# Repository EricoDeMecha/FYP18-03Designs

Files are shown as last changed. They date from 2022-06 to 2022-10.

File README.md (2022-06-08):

## Design and Fabrication of an Automated Discharge Collection Unit of a Synthetic Hdyro-Experimental Machine

Latex sources

### Usage
Run ```renamef``` in the source directory to rename the output file.
```bash
    renamef
```

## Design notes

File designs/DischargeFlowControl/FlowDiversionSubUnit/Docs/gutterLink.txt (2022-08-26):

https://www.pvcpipefitting.com/products/110mm-half-round-pvc-rain-gutter/

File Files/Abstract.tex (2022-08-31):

\addcontentsline{toc}{section}{Abstract}
\section*{Abstract}
\label{sec:}
\par
The synthetic hydro-experimental machine used for fluid mechanics experiments in the fluids lab at JKUAT uses a manual mechanical system in the collection of the discharge during experiments such as the determination of coefficient of discharge of the Venturi. The user is required to turn a $1\frac{3}{4} inch $ ball valve in steps determined by human intuition, and for every step,he/she is required to slide a metallic diverter to collect the discharge to a separate tank, and at the same time, to start measuring the temperature of the discharge, and the timer using an analog stop watch. This synchronism is necessary for precise data in the computation of the fluid flow properties but cannot be achieved by human. 
\par
This project intends to design and fabricate an automated discharge collection system to minimize this human error while maintaining the credibility of the experiment. A modular system has been designed comprising of three major units; a discharge flow control unit, a discharge handling unit, and an interface and control unit. Through a touch-LCD interface, the user will set either the time interval between steps in an experiment or the number of steps for an experiment. In either case, the system will automatically determine the other based on the calibration of a full step. An MG996R servo motor has been selected to control the flow in steps that can be less than $1^{0}$ and for every step, a LA-T8 micro-linear actuator has also been selected to drive an oscillating flap through a four-bar kinematic chain. The flap diverts the flow to a discharge collection tank where its temperature and weight are measured using the selected DS18B20 temperature sensor, and four 50Kg strain type load cells connected in a WheatStone bridge respectively. The data for every step are displayed on the interface. The collected discharge is then emptied to the main reservoir through a solenoid valve before the next step.

\par
This automation will reduce the error margin in the computation of fluid flow properties due to the human error.

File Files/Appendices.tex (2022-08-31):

\appendix
\section{Appendix}

\subsection{Nema 17 Stepper motor dimensions}
    \begin{figure}[H]
        \centering
        
        \caption{Nema 17 Stepper Motor Drawing}
    \end{figure}

\subsection{Ball valve dimensions}
    \begin{figure}[H]
        \centering
        
        \caption{Ball valve socket}
    \end{figure}

\subsection{MG996R Servo motor dimensions}
\begin{figure}[H]
    \centering
    
    \caption{MG996R Servo Motor}
\end{figure}

\subsection{Synthetic Hydro Experimental Machine in JKUAT}
\begin{figure}[H]
    \centering
    
    \caption{S.H.E.M relevant machine dimensions}
\end{figure}

\subsection{Semester 1 \& 2 Time Plan}

\begin{table}[H]
\centering
\begin{tabular}{|ll|l|l|l|l|l|l|l|l|l|l|}
\hline
\multicolumn{1}{|l|}{\textbf{Week}} & \textbf{1} & \textbf{2} & \textbf{3} & \textbf{4} & \textbf{5} & \textbf{6} & \textbf{7} & \textbf{8} & \textbf{9} & \textbf{10} & \textbf{11} \\ \hline
\multicolumn{1}{|l|}{Project proposal} &  & \cellcolor[HTML]{656565}{\color[HTML]{656565} } & \cellcolor[HTML]{656565}{\color[HTML]{656565} } & \cellcolor[HTML]{656565}{\color[HTML]{656565} } &  &  &  &  &  &  &  \\ \hline
\multicolumn{1}{|l|}{Continuous Presentation} &  &  &  &  & \cellcolor[HTML]{656565} & \cellcolor[HTML]{656565} & \cellcolor[HTML]{656565} & \cellcolor[HTML]{656565} & \cellcolor[HTML]{656565} & \cellcolor[HTML]{656565} & \cellcolor[HTML]{656565} \\ \hline
\multicolumn{1}{|l|}{Literature review} &  &  &  &  &  & \cellcolor[HTML]{656565} & \cellcolor[HTML]{656565} & \cellcolor[HTML]{656565} & \cellcolor[HTML]{656565} & \cellcolor[HTML]{656565} & \cellcolor[HTML]{656565} \\ \hline
\multicolumn{1}{|l|}{Discharge flow control design} &  &  &  &  &  & \cellcolor[HTML]{656565} & \cellcolor[HTML]{656565} & \cellcolor[HTML]{656565} & \cellcolor[HTML]{656565} & \cellcolor[HTML]{656565} &  \\ \hline
\multicolumn{2}{|l|}{Discharge   collection unit design} &  &  &  &  &  & \cellcolor[HTML]{656565} & \cellcolor[HTML]{656565} & \cellcolor[HTML]{656565} & \cellcolor[HTML]{656565} &  \\ \hline
\multicolumn{1}{|l|}{Interface and control design} &  &  &  &  &  &  &  &  & \cellcolor[HTML]{656565} & \cellcolor[HTML]{656565} & \cellcolor[HTML]{656565} \\ \hline
\multicolumn{1}{|l|}{Assembly and testing} &  &  &  &  &  &  & \cellcolor[HTML]{656565} & \cellcolor[HTML]{656565} & \cellcolor[HTML]{656565} & \cellcolor[HTML]{656565} &  \\ \hline
\multicolumn{1}{|l|}{Interim report} &  &  &  &  &  &  &  &  & \cellcolor[HTML]{656565} & \cellcolor[HTML]{656565} & \cellcolor[HTML]{656565} \\ \hline
\multicolumn{1}{|l|}{Final presentation} &  &  &  &  &  &  &  &  &  &  & \cellcolor[HTML]{656565} \\ \hline
\end{tabular}
\caption{Semester 1 timeplan}
\end{table}

\begin{sidewaystable}
\centering
\caption{Semester 2 Timeplan}
\resizebox{\linewidth}{!}{%
\begin{tabular}{|>{\hspace{0pt}}m{0.392\linewidth}|>{\hspace{0pt}}m{0.035\linewidth}|>{\hspace{0pt}}m{0.035\linewidth}|>{\hspace{0pt}}m{0.035\linewidth}|>{\hspace{0pt}}m{0.035\linewidth}|>{\hspace{0pt}}m{0.035\linewidth}|>{\hspace{0pt}}m{0.035\linewidth}|>{\hspace{0pt}}m{0.035\linewidth}|>{\hspace{0pt}}m{0.035\linewidth}|>{\hspace{0pt}}m{0.035\linewidth}|>{\hspace{0pt}}m{0.035\linewidth}|>{\hspace{0pt}}m{0.035\linewidth}|>{\hspace{0pt}}m{0.035\linewidth}|>{\hspace{0pt}}m{0.035\linewidth}|>{\hspace{0pt}}m{0.035\linewidth}|>{\hspace{0pt}}m{0.035\linewidth}|} 
\hline
\textbf{Week} & \textbf{14} & \textbf{15} & \textbf{16} & \textbf{17} & \textbf{18} & \textbf{19} & \textbf{20} & \textbf{21} & \textbf{22} & \textbf{23} & \textbf{24} & \textbf{25} & \textbf{26} & \textbf{27} & \textbf{28} \\ 
\hline
Design for fabrication & {\cellcolor[rgb]{0.471,0.471,0.471}} &  &  &  &  &  &  &  &  &  &  &  &  &  &  \\ 
\hline
Generating fabrication files & {\cellcolor[rgb]{0.471,0.471,0.471}} & {\cellcolor[rgb]{0.471,0.471,0.471}} &  &  &  &  &  &  &  &  &  &  &  &  &  \\ 
\hline
Procurement of fabrication materials &  & {\cellcolor[rgb]{0.471,0.471,0.471}} & {\cellcolor[rgb]{0.471,0.471,0.471}} &  &  &  &  &  &  &  &  &  &  &  &  \\ 
\hline
Procurement of electrical and electronics components &  &  & {\cellcolor[rgb]{0.471,0.471,0.471}} & {\cellcolor[rgb]{0.471,0.471,0.471}} &  &  &  &  &  &  &  &  &  &  &  \\ 
\hline
Fabrication of the discharge flow control unit(DFCU) &  &  & {\cellcolor[rgb]{0.471,0.471,0.471}} & {\cellcolor[rgb]{0.471,0.471,0.471}} & {\cellcolor[rgb]{0.471,0.471,0.471}} &  &  &  &  &  &  &  &  &  &  \\ 
\hline
Writing drivers and firmware for the electronics in DFCU &  &  &  &  & {\cellcolor[rgb]{0.471,0.471,0.471}} & {\cellcolor[rgb]{0.471,0.471,0.471}} &  &  &  &  &  &  &  &  &  \\ 
\hline
Assembly and testing of the DFCU &  &  &  &  &  &  & {\cellcolor[rgb]{0.471,0.471,0.471}} &  &  &  &  &  &  &  &  \\ 
\hline
Fabrication of the discharge handling unit(DHU) &  &  &  &  &  &  &  & {\cellcolor[rgb]{0.471,0.471,0.471}} & {\cellcolor[rgb]{0.471,0.471,0.471}} & {\cellcolor[rgb]{0.471,0.471,0.471}} &  &  &  &  &  \\ 
\hline
Writing drivers and firmware for the electronics in DHU &  &  &  &  &  &  &  &  &  & {\cellcolor[rgb]{0.471,0.471,0.471}} & {\cellcolor[rgb]{0.471,0.471,0.471}} &  &  &  &  \\ 
\hline
Assembly and testing of the DHU &  &  &  &  &  &  &  &  &  &  &  & {\cellcolor[rgb]{0.471,0.471,0.471}} &  &  &  \\ 
\hline
Development of the LCD driver and GUI &  &  &  &  &  &  &  &  &  &  &  & {\cellcolor[rgb]{0.471,0.471,0.471}} & {\cellcolor[rgb]{0.471,0.471,0.471}} &  &  \\ 
\hline
Assembly and testing of the system &  &  &  &  &  &  &  &  &  &  &  &  &  & {\cellcolor[rgb]{0.471,0.471,0.471}} &  \\ 
\hline
Final Presentation &  &  &  &  &  &  &  &  &  &  &  &  &  &  & {\cellcolor[rgb]{0.471,0.471,0.471}} \\
\hline
\end{tabular}% <-- Remember this
}
\end{sidewaystable}

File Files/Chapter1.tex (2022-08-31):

\section{Introduction}
\label{sec:introduction}
\subsection{Background}
Fluid flow measurement involves the measurement of the properties of a smooth and uninterrupted stream of flowing particles that conform to a pipe. These flow properties include the coefficient of discharge, mass flow rate, fluid velocity, differential pressure, and conductivity coefficients \cite{pereira2009flow}. They are altered and measured by flow measuring devices such as the Venturi, the Orifice, turbine flow meters and rotameters \cite{nandagopal2022fluid}. These measurements are finally related to the flow using the Bernoulli's equation. 

\par
The Synthetic Hydro-Experimental machine, currently installed in JKUAT, is a configurable machine with these flow meters. This machine is used to conduct experiments to establish relationships between the fluid flow properties and the behavior of the flow. It has a lift pump, gate valves, alcohol manometers, pressure gauges, a Pelton turbine, a Venturi, an orifice, and water reservoirs.  During experiments, the lift pump is turned on, and the discharge valve is fully opened to establish a steady flow.  The discharge valve is then closed. The valve is opened in small steps depending on the number of steps required. For each step, the discharge is collected, and its temperature is measured within a specific time interval. Finally, the weight of the collected discharge is also measured.

\subsection{Problem statement}

In fluid flow experiments utilizing the Venturi and the orifice to establish the coefficient of discharge, the discharge steps must be precisely opened, and time and temperature measurements must be made concurrently with discharge collection so as to achieve values that are within a reasonable range.The Synthetic Hydro-Experimental machine now in use at JKUAT to establish this relationship, however, is entirely mechanical, making it impossible for a human to do some of the simultaneous measurements. A ball valve regulates the flow rate in small intervals using human intuition, which can be imprecise. As a result, with these discrepancies, the findings might frequently be outside of the acceptable range. Automating the discharge collection process can minimize the error in the results and still preserve the credibility of the experiment.

\subsection{Objectives}
\subsubsection{Main objective}

 To automate the discharge collection process for the Synthetic Hydro-Experimental machine. 

\subsubsection{Specific objectives}

\begin{enumerate}
	\item To design an automated discharge flow control unit that can turn the ball valve in steps of less than $1^{0}$ and divert the flow in less than 1 second.
	\item To design and fabricate a discharge handling unit with automated weight, time and temperature measurements, and a discharge collection tank that can discharge is the least time possible.
    \item To design a graphical user interface and a robust control algorithm to integrate the units.

\end{enumerate}

\subsubsection{Expected outcomes}
A unit with a discharge flow control mechanism that can turn in steps of less than $1^{0}$. Furthermore, to accurately regulate the flow of the discharge into either the collecting tank or into the main reservoir, the mechanism should be able to divert the flow from the pipeline in less than a second. The discharge should then be collected in a  tank that can store up to $0.02m^{3}$ of the discharge. A weight measurement device with a gauge factor of more than 2 to be attached at the bottom of the collection tank.Finally, a graphical user interface that allows for the displaying of measurements in this case temperature, time and weight and control of operations

% \begin{enumerate}
%     \item \textbf{Discharge flow control unit}
%     \begin{itemize}
%         \item \textbf{Flow control subunit}-  A discharge flow control mechanism that can turn steps less than $1^{0}$. This is necessary in a case where an experiment is to be done in more than 90 steps( less than $1^{0}$ per step). 
%         \item \textbf{Diversion subunit} - A mechanism that can divert the flow in less than a second. This is to ensure that only the flow within the time interval is collected.
%     \end{itemize}
%     \item \textbf{Discharge Handling unit}
%     \begin{itemize}
%         \item \textbf{Discharge collection tank}  - A tank that can collect up to $0.02m^{3}$ of the discharge. This is an estimated quantity of the discharge collected when the valve is fully open for approximately 30 seconds.
%         \item \textbf{Discharge Weight measurement} -  A weight measurement device with a gauge factor of more than 2. This is necessary to detect even the smallest change in weight.
%         \item \textbf{Discharge temperature measurement} - An immersible temperature sensor with a resolution of more than 10 bits. This is necessary to detect even the smallest change in the temperature of the discharge.
%         \item \textbf{Outlet valve} - Approximately 1 inch valve in order to empty the empty approximately $0.02m^{3}$ in the least time possible. 
%     \end{itemize}
%     \item \textbf{Interface and Control Unit}
%     \begin{itemize}
%         \item \textbf{Micro-controller} - A microcontroller that can drive a 320x240 touch LCD at approximately 30 frames per second. This is to ensure the displayed data is updated on time while maintaining a slick graphical user interface. 
%         \item \textbf{Application logic} - A robust application logic with auto-calibration capabilities, and event-driven. 
%     \end{itemize}

% \end{enumerate}

\subsection{Justification}
This automation will streamline the discharge collecting process while also ensuring the consistency and quality of the data collected in each phase of the fluid flow tests performed on the system. In contrast to the existing condition, such automation allows a single person to perform the experiment without significant effort. Furthermore, the automated system will also be modular, allowing it to be readily attached and detached from the main machine with few modifications.

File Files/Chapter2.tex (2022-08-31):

\section{Literature Review}
\subsection{Introduction}
Fluid flow experiments involve determination of the flow velocity, the mass flow rate or volumetric flow rate. These experiments are used to familiarize the students with typical methods of flow measurement of an incompressible fluid and, at the same time demonstrate applications of the Bernoulli's equation. Thus, these experimental investigations require the application of measuring techniques to yield quantitative information on the relationship between pressure, temperature and local flow velocities.
\par
The synthetic hydro-experimental machine employs the use of the venture and the orifice meter in determining these fluid properties specifically the coefficient of discharge. It involves determining the relationship between a flowing fluid through a valve, the weight and temperature of the collected discharge. The machine comprises of four main parts; the diverter, gate valve, weight and temperature measurement unit. The measurement involves four main processes, discharge collection, diversion, weight and temperature measurement. 
\subsubsection{Gate Valve }
\par
The valve is attached at the end of the pipeline immediately after the venture and the orifice meter. It is used in flow rate control by either increasing or reducing the aperture at which the fluid flows. The experiment is conducted in several steps which is determined by opening and closing of the valve. At the start of the experiment, the valve is initially closed hence no fluid is collected. Depending on the required number of steps, the valve is then opened in small steps allowing the discharge to be collected for purposes of weight and temperature measurement.
\subsubsection{Diverter }
\par
After each step of the experiment, the collected fluid flows into the weight measurement unit through the help of a diverter. The diverter is used to direct the collected discharge into the weight measurement unit which is located at the periphery of the rig to avoid flowing back into the reservoir. The diverter is a mechanical device that is moved by hand.
\subsubsection{Temperature measurement unit }
\par
 The temperature of the collected discharge is measured immediately after the fluid flows through the gate valve by use of a thermometer. This is to minimize the environmental effects, for instance the effects of the metallic diverters which would otherwise compromise on the temperature readings. The readings are measured and recorded after each step of the experiment.
\subsubsection{Pressure measurement }
\par
The differential manometers are attached just before and after both the venture and the orifice and is used to determine the pressure of the flowing fluid. These manometric readings are recorded after each and every step of the experiment.
\subsubsection{Weight measurement unit }
\par
The final part involves measuring the weight of the collected discharge. This is done by use of a measuring scale with loads attached to it. The above measurements are then used to establish the coefficient of discharge of the fluid.
\subsection{Existing Technologies}
Some advanced and even rudimentary technologies have been used in place of the Synthetic Hydro-Experimental machine for the determination of fluid flow properties. The technologies include :   
\subsubsection{Computational Fluid Dynamics}
Computational fluid dynamics(CFD) is a powerful modelling and analysis technique that utilizes finite difference techniques to solve highly non-linear differential equation of pressure, energy, relative humidity, air temperature and velocity \cite{raman2018review}. It can be used to model fluid flow in flow measurement devices.
\par
Tukimin et al \cite{tukimin2016cfd} in their study  conducted a CFD analysis using an Single Kernel Estimate (SKE) turbulence model to determine the coefficient of discharge of a Venturi tube, and finally compared the results to those obtained from a physical experimental setup. The test loop shown in figure \ref{fig:test_loop_rig} was used both in a physical setup and a CFD model. 

\begin{figure}[ht]

\centering
\caption[Test loop schematic]{ Test loop schematic by Tukimin et al \cite{tukimin2016cfd}}
\label{fig:test_loop_rig}
\end{figure}

They designed a CFD model using the ANSYS Design Modeller software. The model consists of a Venturi tube, designed according to the standards ISO 5167:2003 \cite{carello2013flow}, and a liquid and gas system. They did a physical experiment using the same test matrix used in the numerical simulation model. Finally, they computed the coefficient of discharge of the venturi using equation \ref{eq:2}.  

\begin{equation}
C d=\frac{4 m \sqrt{1-\beta^{4}}}{\pi \varepsilon d^{2} \sqrt{200000 D p_{1} \rho_{1}}}
\label{eq:2}
\end{equation}

\begin{table}[!t]
  \begin{center}
    \leavevmode
    \hangcaption{ Calculated $C_{d}$}   
     \begin{tabular}{rlc}\hline
      Venturi under Test & Average Discharge Coefficient &  Average Discharge Coefficient \\ \hline
       & From experiment &  From CFD post \\ \hline
      Venturi 1 & 0.99366 &  0.984347 \\ \hline
    \end{tabular}
    \label{tab:cd}
  \end{center}
\end{table}
The results obtained in \ref{tab:cd} showed a difference of less than $1 \%$ between the $C_{d}$ obtained from the two setups.
\par
Tamhankar et al \cite{tamhankar2014experimental} also did a similar experiment using a CFD model designed in ANSYS Fluent 13.0 utilizing a Realizable k-$\epsilon$ turbulence model which is superior to a Standard k-$\epsilon$ turbulence model and compared the results to those obtained from an experimental setup show in figure \ref{fig:exp}. 

\begin{figure}[ht]

\centering
\caption[Experimental setup ]{ Experimental setup by Tamhankar et al \cite{tamhankar2014experimental}}
\label{fig:exp}
\end{figure}

Table \ref{tab:results} shows the results obtained from the study
\begin{table}[!t]
    \centering
    \hangcaption{Results}
    \begin{tabular}{|c|c|c|}
        \hline \text { Reading No. } & \text { Experiment } & \text { CFD analysis } \\
        \hline 1 & 0.9724 & 0.9619 \\
        \hline 2 & 0.9592 & 0.9689 \\
        \hline 3 & 0.9779 & 0.9692 \\
        \hline
    \end{tabular}
    \label{tab:results}
\end{table}

The study concluded that difference in values of the coefficient of discharge obtained from the model and those obtained from the experimental setup was less than $ 5 \%$ .
\subsubsection{Analytical Predictions}
This technique utilizes the Bernoulli's equation to establish an analytical correlation between the fluid flow and the coefficient of discharge of the Venturi meter. 

\begin{figure}
    \centering
    
    \caption[Venturi Meter]{Venturi meter \cite{venturi_meter}}
    \label{fig:venturi}
\end{figure}

Figure \ref{fig:venturi} shows the Venturi meter. Assuming the flow is ideal and applying the Bernoulli's equation before and after the contraction, 

\begin{equation}
\begin{aligned}
&\frac{p_{1}}{\rho g}+\frac{v_{1}^{2}}{2 g}+z_{1}=\frac{p_{2}}{\rho g}+\frac{v_{2}^{2}}{2 g}+z_{2} \\
&\text { But } Z_{1}=Z_{2}, \\
&\frac{\left(p_{1}-p_{2}\right)}{\rho}=\frac{\left(v_{2}^{2}-v_{1}^{2}\right)}{2} \\
&\frac{\left(p_{1}-p_{2}\right)}{\rho}=\frac{v_{2}^{2}}{2}\left(1-\frac{A_{2}^{2}}{A_{1}^{2}}\right) \\
&\frac{\Delta p}{\rho}=\frac{v_{2}^{2}}{2}\left(1-\beta^{4}\right) \\
&v_{2}=\frac{1}{\sqrt{1-\beta^{4}}} \sqrt{\frac{2 \Delta p}{\rho}}
\end{aligned}
\label{eq:bernoulli_der}
\end{equation}

Applying the continuity equation to the result of the derivation in \ref{eq:bernoulli_der},
\begin{equation}
\begin{aligned}
&Q_{t h}=A_{1} v_{1}=A_{2} v_{2} \\
&Q_{t h}=A_{2} v_{2}=\frac{1}{\sqrt{1-\beta^{4}}} \frac{\pi d^{2}}{4} \sqrt{\frac{2 \Delta p}{\rho}}
\end{aligned}
\label{eq:mass_flow_rate}
\end{equation}
Equation \ref{eq:mass_flow_rate} of theoretical flow rate is based on the assumption that the flow is steady, incompressible, inviscid, irrotational, no losses and the velocities $V_{1}$ and  $V_{2}$ are constant across the cross section \cite{arun2015prediction}. 

\begin{equation}
\mathrm{Q}_{\mathrm{act}}=\frac{\mathrm{C}_{\mathrm{d}_{\mathrm{st}} \mathrm{d}}}{\sqrt{1-\beta^{4}}} \frac{\pi \mathrm{d}^{2}}{4} \sqrt{\frac{2 \Delta \mathrm{p}}{\rho}}
\end{equation}
The frictional and viscous losses in a laminar flow can be estimated by the Darcy's law
\begin{equation}
\mathrm{H}_{\mathrm{L}}=\frac{(\Delta \mathrm{p})_{\text {viscous }}}{\rho \mathrm{g}}=\mathrm{f} \frac{\mathrm{v}^{2}}{2 \mathrm{~g}} \frac{\mathrm{D}}{\mathrm{D}}
\end{equation}
where 'f' is the friction factor.
\par
Coefficient of discharge equation \ref{eq:cd2} where for laminar flow, 'f' is given by equation \ref{eq:f} . This equation is derived from both the Darcy's law equation and the theoretical flow rate equation \ref{eq:mass_flow_rate}.
\begin{equation}
f=\frac{64}{R_{e d}}
\label{eq:f}
\end{equation}

\begin{equation}
C_{\mathrm{d}}=0.995 \sqrt{\frac{1}{(1+3 f)}}
\label{eq:cd2}
\end{equation}

\par
Arun et al \cite{arun2015prediction} did  a comparision of the $C_{d}$ obtained by this method and that obtained from a CFD simulation. The study concluded that the results from the two methods had an uncertainty of $0.9\%$.
\subsection{Related Works}
Discharge collection techniques have been developed for various applications. Some of these applications are related to the discharge collection unit used in the Synthetic Hydro-Experimental machine.

\subsubsection{Electromagnetic activation}
Angelo et al \cite{odetti2019design} implemented this technique in the design and testing of an Modular Automatic Water Sampler(MAWS). They designed MAWS and mounted them on unmanned marine vehicle with the aim of collecting water samples for scientific campaigns in front of polar tidewater glaciers. Their main design considerations was the response time of the stopper since the MAWS were operated under water and at the risk of damage by glaciers. The actuation unit of the sampler is shown in figure \ref{fig:stopper}. 

\begin{figure}
    \centering
    
    \caption[Sampler actuation mechanism]{Sampler actuation mechanism \cite{odetti2019design}}
    \label{fig:stopper}
\end{figure}

When the coil in the solenoid is crossed by a current a strong magnetic field is generated that attracts the ferromagnetic plunger connected to the sealing stopper and opens the bottle allowing water to flow into the bottle's neck. As the current stops the two permanent magnets attract each other and the stopper seals the bottle \cite{odetti2019design}.

\subsubsection{Pneumatic Control}
Pneumatic actuators utilizes the power of compressed air to impart motion on objects. Sangmin, and Joonwon \cite{lee2009development} did a design of cartridge-type pneumatic dispenser with a back flow stopper. The system used a membrane covering a discharge hole. The membrane was opened and closed using negative and positive pneumatic pressure respectively as shown in figure \ref{fig:dispensing_mechanisml}. 

\begin{figure}
    \centering
    
    \caption[Dispensing mechanism]{Dispensing mechanism \cite{lee2009development}}
    \label{fig:dispensing_mechanisml}
\end{figure}

The application was able to do precise dispensation of 100nL to 400nL droplets.

\subsection{Summary}

Every fluid flow experiment done on the Synthetic Hydro-Experimental machine involves the collection of discharge and the measurement of its properties. The most common experiment is the determination of the coefficient of discharge  of the Venturi and the Orifice. In this literature, other techniques such as CFD and analytical methods have been found to be effective as alternatives to this machine. These techniques have been proven to produce results with a difference of less than $1\%$  from the experimental results obtained from a physical setup. Such results can also be obtained from the fluids rig currently used in JKUAT by automating the discharge collection unit. With regard to this, the literature has also covered discharge collection techniques that have proven to be effective in other applications and can be adapted for this automation. This techniques include the application of pneumatics and electromagnetism. 

\subsection{Gap analysis}
\begin{enumerate}
    \item The use of the CFD method or the analytical method  undermines the credibility of the fluid flow experiments. This two techniques are rather used for the design of fluid flow measuring devices.
    \item CFD method can also be very resource intensive in terms of compute resources. Softwares used for this method requires a hefty license fee.
    \item The application of the analytical method involves tedious calculations and several assumptions which can produce untrustworthy results.
    \item The use of the Synthetic Hydro-Experimental machine with a manual discharge collection unit often produce results with huge error margins.  
\end{enumerate}

This project is entirely focused on addressing gap number four with the application of techniques such as pneumatics or electromagnetism. This closes in the technological gap with the use of CFD, and simplify the use of analytical methods by providing data for the computation of fluid flow properties.

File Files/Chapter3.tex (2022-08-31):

\section{Methodology}
\subsection{Overview}
This project consists of three main units: a discharge flow control unit, a discharge handling  unit, and a software and control unit. 
\subsection{Discharge flow control unit}
This unit consist of two main sub-units:
\begin{enumerate}
    \item \textbf{Flow control sub-unit} -
    This sub-unit controls the dispensing of the discharge from the discharge pipe in steps.
    \item \textbf{Flow diversion sub-unit} -
    This sub-unit diverts the discharge from the main discharge pipe either to the discharge collection tank or to the main reservoir.
\end{enumerate}
\par
\subsubsection{Flow control  sub-unit}
The current state-of-art of this unit is as shown in Figure \ref{fig:current_discharge_control_unit}. 
\begin{figure}[H]
    \centering
    
    \caption{Current discharge control unit}
    \label{fig:current_discharge_control_unit}
\end{figure}
\par
The $1 \frac{3}{4} inch $ ball valve on the main discharge pipe is opened in steps by hand using the lever. The size of a step is determined by intuition.
\par
\textbf{Design}\\
To ensure minimum modification of the existing machine, the automation of this unit utilized the existing ball valve. The opening and closing of the valve is automated using a motorized system that can open the valve in precise steps.
\par
\textbf{Motor}
\par
The selection and the sizing of the motor for this application was based on the following considerations:

\begin{enumerate}
    \item The torque required to open and close the ball valve.
    \item The steps size or the number of steps the system can open the valve.
\end{enumerate}
\par
Based on these two considerations, the following two applications were considered.
\begin{enumerate}
    \item \textbf{Stepper motor application}\\
    This motor operates by accurately synchronizing position with the pulse signal output from the controller to the driver thus achieving highly accurate positioning and speed control. Stepper motors feature high torque and low vibration at low speeds ideally below 1500rpm, ideal for applications requiring quick fixed positioning in a short distance \cite{wargula2017investigations}. Furthermore, stepper motor rotates with a fixed step angle typically 1.8 degrees for a 2-phase. However, to achieve this requires the use of a micro-step driver.
    \par
    Besides having full control of rotation and speed, the simple structure of stepper motors is achieved without using electrical components, such as an encoder within the motor. For this reason, stepper motors are very robust and have high reliability with very few failures. As for stopping accuracy, ±0.05° (without cumulative pitch errors) is very accurate\cite{wargula2017investigations}. Because the positioning of stepper motors is performed by open-loop control, and operated by the magnetized stator and magnetic rotor with small teeth, stepper motors have a higher follow-up mechanism toward commands than the servo motors. Also, no hunting occurs when stopping it.
    
    \textbf{Design with stepper motor}
    \begin{enumerate}
    \item \textbf{Motor selection}\\
    From the stepper motors available in the market, Nema 17 Stepper motor shown in figure \ref{fig:Nema17 Steppper motor} was the best choice for the job since it can produce a $1.8^0$ step out of the box without a microstep driver. With the help of a microstep driver, it can produce as small as $1^0$ step.
    \begin{figure}[H]
        \centering
        
        \caption[Nema 17 Stepper motor]{Nema 17 Stepper motor \cite{nema17}}
        \label{fig:Nema17 Steppper motor}
    \end{figure}
    \par
    Its technical specifications are as shown in the table \ref{tab:nema17_specs}:
\begin{longtable}{|l|l|}
\caption[Nema 17 Stepper Motor Technical specification]{Nema 17 Stepper Motor Technical specifications \cite{nema17}}
\label{tab:nema17_specs}\\
\hline
\textbf{Property} & \textbf{Value} \\ \hline
\endfirsthead
%
\multicolumn{2}{c}%
{{\bfseries Table \thetable\ continued from previous page}} \\
\hline
\textbf{Property} & \textbf{Value} \\ \hline
\endhead
%
Rated Voltage & 12V DC \\ \hline
Current & 1.2A at 4V \\ \hline
Step Angle & 1.8 deg \\ \hline
No. of Phases & 4 \\ \hline
Motor Length & 1.54 inches \\ \hline
4-wire, 8 inch lead &  \\ \hline
steps per revolution & 200 \\ \hline
Operating Temperature & -10 to 40 °C \\ \hline
Unipolar Holding Torque & 22.2 oz-in \\ \hline
Maximum torque & 4.8 Kg.cm \\ \hline
\end{longtable}

    \item \textbf{Ball valve - motor interface}
    \par
    An interface is required to connect the motor rotor to the ball valve. The following  two design options were considered for this application:
    \begin{itemize}
        \item An interface that could fit the rotor on one end and with claw-like fingers on the other end to turn the existing ball valve's lever.
        \item An interface that could fit the rotor on one end and with the other end, similar to the lever, that could be used in place of the lever.
    \end{itemize}
    \par
    The second option was chosen since the first choice will introduce a lag in a turn action since the point of action on the lever is displaced from the line of rotation of the rotor.
    \begin{figure}[H]
        \centering
        
        \caption{Interface}
        \label{fig:Interface}
    \end{figure}
    Figure \ref{fig:Interface} shows the interface design. Dimensions of the interface, such as the width of its base, were measured and transferred from the existing lever.
    \par
    \item \textbf{Motor cage}
    \par
    In order to support the motor on the ball valve, a motor cage was designed to fit the motor as shown in Figure \ref{fig:motor_cage_stepper}.
    
    \begin{figure}[H]
        \centering
        
        \caption{Motor Cage}
        \label{fig:motor_cage_stepper}
    \end{figure}
    
    The dimensions of the motor cage in figure \ref{fig:motor_cage_stepper} were determined from that of the stepper motor, the motor-ball valve interface, and that of the existing ball valve socket in order to fit the socket.
    
    \item \textbf{Straps}
    \par
    The motor cage with the stepper motor mounted is mounted on the main discharge pipe using straps, one of which is shown in figure \ref{fig:mounting_straps_stepper}.
    
    \begin{figure}[H]
        \centering
        
        \caption{Mounting straps}
        \label{fig:mounting_straps_stepper}
    \end{figure}
 \item \textbf{Assembly of discharge flow control using stepper}
    \par
    The assembly of the discharge control unit is as shown in figure \ref{fig:stepper_actuated_ball_valve}. Nuts are used to fasten the whole structure on the main discharge pipe.
    
    \begin{figure}[H]
        \centering
        
        \caption{Stepper Actuated ball valve}
        \label{fig:stepper_actuated_ball_valve}
    \end{figure}
    
    % \item \textbf{Finite element analysis of the assembly}
    % \par
    % The assembly was stress tested by applying a torque on the motor cage to determine if it could hold at the maximum torque of the motor. To do this, each part of this assembly was be assigned a material. Polyactic acid (PLA) was selected as the common material for all of the parts in the assembly. This is majorly due to the following reasons:
    % \begin{itemize}
    %     \item The maximum weight of the part to be supported by the structure is the stepper motor's weight, 450 grams. This can be supported by a 3D printed plastic support. A lighter material such as fiber glass or carbon fiber could be used but they are costlier than the set project's budget.
    %     \item The parts are complex for fabrication on the currently existing machinery in the university.
    % \end{itemize}
    % \item \textbf{Results}
    % \par
    % As shown in figure \ref{fig:SimulationResults}, the structure holds for the maximum torque of a Nema 17 stepper motor, $4.9 kg.cm$ or $0.4707192 Nm$.
    % \begin{figure}[H]
    %     \centering
    %     \includegraphics[width=\textwidth]{Figures/ActuatedBallValve-Static-1-1-1.png}
    %     \caption{Simulation results}
    %     \label{fig:SimulationResults}
    % \end{figure}

    \end{enumerate}

    \item \textbf{Servo motor application}\\
    Servo motors run significantly faster than stepper motors, with speeds greater than 1500 rpm \cite{halicioglu2016mechanisms}. This enables servomotors to be used with gearboxes to deliver much higher torque at useful speeds. They also deliver more consistent torque across the speed range of the motor. Unlike stepper motors, they do not have holding torque. Closed-loop operation enables the controller/drive to command that the load remain at a specific position, however, and the motor will make continual adjustments to hold it there. Thus, servomotors can produce de facto holding torque\cite{halicioglu2016mechanisms}. The Servo motor rotates with a fixed step angle as low as 1 degree with or without the use of a driver. Furthermore, when powered, servomotors tend to move their shaft position to zero, a phenomenon known as hunting.
    \par
    \textbf{Design with servo motor}
    \begin{enumerate}
    \par
    \item \textbf{Motor selection}
    \par
    An MG996R Servo motor shown in figure \ref{fig:servo_motor_assembly} was the best choice among many servo motors found in the market. It is the motor that provided the torque required to turn the ball valve at an optimum price for the project's budget. 
    \par
    The motor specification as shown in table \ref{tab:MG996R_servo_specs}.
    \begin{table}[H]
    \centering
    \caption[MG996R Servo motor specifications]{MG996R Servo motor specifications \cite{mg996r}}
    \begin{tabular}{|l|l|}
    \hline
    \textbf{Property} & \textbf{Value} \\ \hline
    Operating Voltage & +5V \\ \hline
    Current & 2.5A (6V) \\ \hline
    Stall Torque & 9.4 kg/cm (at 4.8V) \\ \hline
    Maximum Stall Torque & 11 kg/cm (6V) \\ \hline
    Operating speed & 0.17 s/60° \\ \hline
    Gear Type & Metal \\ \hline
    Rotation & 0°-180° \\ \hline
    Weight of motor & 55gm \\ \hline
    \end{tabular}
    \label{tab:MG996R_servo_specs}
    \end{table}
    \begin{figure}[H]
        \centering
        
        \caption[MG996R servo motor]{MG996R servo motor \cite{mg996r}}
        \label{fig:servo_motor_assembly}
    \end{figure}
    The mounting mechanism of a servo motor is not as direct as that of the stepper motor since a servo motor homes to $0^{0}$ on powering. It is required that the home position of the servo motor is equal to the closed position of the ball valve. Therefore, during mounting, the servo motor must be rotated to align its home position with the closed position of the ball valve.
    \par
    The mounting mechanism should therefore allow for this rotation. A cuboid cage could have been used to support the motor in place, but since the centre of mass of this motor is displaced from its line of axle rotation, rotating the cuboid could mean repositioning the support stands for the cuboid.
    \par
     There were two options that could achieve this kind of rotation:
     \begin{enumerate}
         \item A combination of a cuboid cage on a circular plate. The cuboid cage could hold the motor while the plate allows the rotation of the assembly of the two without the need of repositioning the stands holding the assembly on the ball valve.
         \par
         \textbf{Designs with this approach}
         \par
         \begin{itemize}
             \item \textbf{Servo motor cage}
            \par
            The cage shown in figure \ref{fig:servo_motor_cage} is screwed on to the motor flaps. It just adds additional mounting points for the motor. 
            \begin{figure}[H]
                \centering
                
                \caption{Servo motor cage}
                \label{fig:servo_motor_cage}
            \end{figure}
            \par
            % \item \textbf{Mounting plate}
            % \par
            % Figure \ref{fig:servo_motor_mounting_plate} shows the mounting plate for the motor cage. The plate is like a ring with slots. The design allows for rotation without the need to reposition the supporting rods. 
            % \par
            % \begin{figure}[H]
            %     \centering
            %     \includegraphics[height=.7\textheight]{Figures/ServoMotorHolderMount.PNG}
            %     \caption{Servo motor mounting plate}
            %     \label{fig:servo_motor_mounting_plate}
            % \end{figure}
            \par
            \item \textbf{The holder assembly}
            \par
            Figure \ref{fig:servo_motor_mounted_assembly} shows the servo motor cage with the servo motor mounted on the mounting plate. The servo motor assembly can be rotated and translated to reposition the line of rotation of the motor axle. 
            \begin{figure}[H]
                \centering
                
                \caption{Servo motor mounted assembly}
                \label{fig:servo_motor_mounted_assembly}
            \end{figure}
             This design can allow for both rotational and translational adjustments along the slots. However, it is complex and require a lot of fasteners.
         \end{itemize}
         \item A combination of spur gears to always translate the line of rotation of the motor axle to a fixed line of rotation no matter the orientation of the motor.
         \clearpage
         \textbf{Designs with the spur gears approach}
         \par
          \begin{itemize}
              \item \textbf{Spur gears}
              \par
              Spur gear shown in Figure \ref{fig:spur_gear} translates the line of rotation by 5.75mm in any orientation of the servo to a fixed centre line.
              \begin{figure}[H]
                  \centering
                  
                  \caption{Spur gear}
                  \label{fig:spur_gear}
              \end{figure}
              \par 
              \item  \textbf{Servo motor-spur gear assembly}
              \par
              Figure \ref{fig:servo_motor_with_spur_gears} shows the spur gear translation system assembled with the servo motor.
              \begin{figure}[H]
                  \centering
                  
                  \caption{Servo motor with spur gears}
                  \label{fig:servo_motor_with_spur_gears}
              \end{figure}
              This design is quite simpler than the first approach. The design considerations are few and can produce even finer translations in the scale of the spur gear pitch($1 mm$). However, the main challenge with this design is the durability of spur gears made of PLA material since servo motors tend to have a high starting torque. This will almost necessitate the replacement of the gears after every two or three experiments.  
          \end{itemize}
     \end{enumerate}
     \par
     Between the two mounting designs described, the first options had more merits than the second option. It might require more material to produce it but at least it is only for one time unlike with second option where the gears are to be replaced after every two or three times in operation.
     \par 
     \item \textbf{Mounting rod}
     \par
     Two of the rod shown in figure \ref{fig:mounting_rods} are used to support the mounted servo motor assembly on the ball valve. The design was such that it allowed for fasteners on both sides: at one end, to fasten the servo motor assembly after alignment and at the other end, to fasten the whole flow control unit on the main discharge pipe.
     \par
     The protrusion of its surface eliminates the need for another fastener. 
      \begin{figure}[H]
          \centering
          
          \caption{Mounting rods}
          \label{fig:mounting_rods}
      \end{figure}
      \par
    \item \textbf{Interface}
    \par
    The interface shown in Figure \ref{fig:interface2} is an improvement from the interface that was used with the stepper motor. This design is minimalistic and requires a lesser volume of material to produce. In addition, it also has provisions(hooks) to allow for even finer adjustments in the first approach for mounting the servo motor.
    \begin{figure}[H]
        \centering
        
        \caption{Interface}
        \label{fig:interface2}
    \end{figure}
    \par
    \item \textbf{Straps}
    \par
    Serrated straps shown in \ref{fig:two_rail_serrated_straps} are also an improvement on the straps used in the stepper motor approach. The serration provide more grip on the discharge pipe. It can also support more load. The sizing and dimensioning was guided by the existing ball valve casing.
    \begin{figure}[H]
        \centering
        
        \caption{Top strap}
        
        \caption{Bottom strap}
        \label{fig:two_rail_serrated_straps}
    \end{figure}
      
    \par
    \item \textbf{Servo motor discharge flow control assembly}
    \par
    The assembly of parts used in the servo motor approach is as shown in Figure \ref{fig:servo_motor_discharge flow control assembly}.
     \begin{figure}[H]
         \centering
         
         \caption{Servo motor discharge flow control assembly}
         \label{fig:servo_motor_discharge flow control assembly}
     \end{figure}
      
    %  \par
    %  \item \textbf{Finite element analysis of the assembly}
    %  \par
    %  PLA material was assigned to each part of the structure. The maximum load torque of the servo motor($11kg.cm$) was then applied on the mounting plate of the motor. The results of the simulation were as shown in figure \ref{fig:servo_assembly_results}. From the results, the structure still holds to the maximum torque with minimal displacement.
    %  \begin{figure}[H]
    %      \centering
    %      \includegraphics[width=\textwidth]{Figures/ServoHolderBallValveAssembly-Static-1-1-1.png}
    %      \caption{Servo Assembly simulation results}
    %      \label{fig:servo_assembly_results}
    %  \end{figure}
    \end{enumerate}
\end{enumerate}

From these two design approaches, the servo motor approach was selected.

\subsubsection{Flow diversion sub-unit}
The design of this unit was based on the following two considerations:
\begin{enumerate}
    \item A faster response time. The response time in this application is the time it takes to divert the discharge flow into the main reservoir or the discharge collection tank. 
    \item An actuator that can provide linear translation of not less than 30 mm. In fact the longer the better. This is measured from the design assembly. This ensures that the discharge is fully diverted into the collection tank or to the main reservoir. 
\end{enumerate}

Based on the above two considerations, the following two design options were feasible.
\begin{enumerate}
    \item \textbf{Piezo-electric actuator}
    \par
    Piezoelectric actuators are transducers that convert electrical energy into a mechanical displacement or stress based on a piezoelectric effect, or vice versa. They are widely used as a high-precision positioning mechanism since they can control a small mechanical displacement at high speed, with the advantages of large generated force, stable displacement, and ease of use\cite{gao2020piezoelectric}. 
    \par
    Among the many advanced piezoelectric actuators on the market, a Xeryon Precision XLA-Series 3 piezo actuator shown in Figure \ref{fig:piezo_actuator} was selected since it satisfied all the design requirements required for this subunit.
    \begin{figure}[H]
        \centering
        
        \caption[Xeryon-XLA Series 3 piezo actuator]{Xeryon-XLA Series 3 piezo actuator \cite{xla3}}
        \label{fig:piezo_actuator}
    \end{figure}
    Its technical specifications are as shown in table \ref{tab:XLA_stuff}.
    \begin{table}[H]
    \centering
      \caption[XLA series 3 piezo actuator specifications]{XLA series 3 piezo actuator specifications \cite{xla3}}
    \begin{tabular}{|l|l|}
    \hline
    \textbf{Property} & \textbf{Value} \\ \hline
    Stroke Length & 45mm \\ \hline
    Resolution & 312nm \\ \hline
    Operating voltage & 20-48V \\ \hline
    Control & Closed loop control with an external XD-A controller \\ \hline
    Temperature & -30  to 70 \\ \hline
    Holding\& Driving  force & 3N \\ \hline
    Speed range & 2mm / s to 400mm / s \\ \hline
    \end{tabular}
    \label{tab:XLA_stuff}
    \end{table}

    From the technical specifications in the table, it is evident that this actuator could be the best choice for this application. However, it requires an external proprietary controller for closed-loop control. Xeryon company products are also not available in public stores such as Amazon or Aliexpress.
    
    \item \textbf{Electromagnetic Actuator}
    \par
    Electromagnetic actuators work on the principle of electromagnetism. Electrical energy is converted to a linear translational mechanical motion and vice versa. The electric current serves as the actuator quantity in electromagnetic actuators.
    \par
    Based on the design considerations, a LA-T8 micro linear actuator shown in figure \ref{fig:la_t8_linear_actuator}  was selected for this application.
    \begin{figure}[H]
        \centering
        
        \caption[LA-T8 linear actuator]{LA-T8 linear actuator \cite{la_t8}}
        \label{fig:la_t8_linear_actuator}
    \end{figure}
    Its technical specifications are shown in table \ref{tab:la_t8_tab}.
    \begin{table}[H]
    \centering
       \caption[LA-T8 Micro-linear actuator technical specifications]{LA-T8 Micro-linear actuator technical specifications \cite{la_t8}}
    \begin{tabular}{|l|l|}
    \hline
    \textbf{Property} & \textbf{Value} \\ \hline
    Operating voltage & 12V DC \\ \hline
    Stroke length & 100mm \\ \hline
    Stroke speed & 150mm/s \\ \hline
    Maximum load & 6.4N \\ \hline
    \end{tabular}
    
    \label{tab:la_t8_tab}
    \end{table}
    From the technical specifications in the table, it is also evident that this actuator satisfies optimumly the requirements required for this application. Unlike the piezo actuator, this device is available for less than \$ 35 in e-Commerce stores such as Amazon or AliExpress.
\end{enumerate}
Based on the above descriptions, the LA-T8 micro-linear actuator was selected for this application mainly because of its availability.
\par
In order to hold this actuator in position the following designs were made:
\begin{enumerate}
    \item \textbf{Electromagnetic Actuator holder}
    \par
    This unit supports the actuator on the ball valve. It is required that this unit will withstand the weight of both the actuator and the diverter. It design is as shown in figure \ref{fig:electromagnetic_actuator}.
    \begin{figure}[H]
        \centering
        
        \caption{Electromagnetic actuator holder}
        \label{fig:electromagnetic_actuator}
    \end{figure}
    The dimensions of this holder design were determined from the dimensions of the LA-T8 linear actuator plus a clearance of 0.5mm.
    
    \item \textbf{Diversion Flap}
    \par
    In order to divert the flow, a channel-like flap is to be used. The design of the flap is as shown in figure \ref{fig:diversion_flap}. 
    \begin{figure}[H]
        \centering
        
        \caption{Diversion flap}
        \label{fig:diversion_flap}
    \end{figure}
    The design was such that it can tap the whole stream from the $1\frac{3}{4} inch$ main discharge pipe on the main machine. Its 150mm length is determined by the length of the gap between the discharge pipe and the collection unit.
    \item \textbf{Flap support frame}
    \par
    This structure supports the diversion flap in place below the discharge pipe. This design was necessary since there is no convenient mounting point on the main machine that can allow the flap to be mounted without making changes to the main machine. It design is as shown in figure \ref{fig:flap_support_frame}.
    \begin{figure}[H]
        \centering
        
        \caption{Flap support frame}
        \label{fig:flap_support_frame}
    \end{figure}
    This frame also provides an extension for supporting the kinematic chain that flexes the flap. 
    \item \textbf{Link}
    \par
    The link serves to connect the linear actuator to the flap. The design is such that, on one side it hinges onto the end of the 100mm actuator while on the other side it is attached to the flap. The linear(forward and backward) movement of the actuator moves the flap to either to direct the discharge into the main reservoir or into the collection tank.
    \begin{figure}[H]
        \centering
        \includegraphics [width=\textwidth]{Figures/RockerLink.PNG}
        \caption{Link}
        \label{fig:my_label}
    \end{figure}
    % \par
    % To amplify the 100mm translation in order to flex the flap enough, a four-bar kinematic mechanism is used. The lengths of the links and the orientation of the four bars are determined by assuming a translation of 100mm at the output.
    % \par
    % Using the MechDesigner software, the kinematic chain was designed to provide the required motion for the flap. The CAM data from its simulation was exported automatically to a SolidWorks model of the fixed point of the part.
    % \begin{enumerate}
    %     \item \textbf{Crank}
    %     \par
    %     The input translation from the linear electromagnetic actuator. The design of this link is as shown in figure \ref{fig:crank}.
    %     \begin{figure}[H]
    %         \centering
    %         \includegraphics{Figures/KLink3.PNG}
    %         \caption{Crank}
    %         \label{fig:crank}
    %     \end{figure}
    %     The connection between this link, the end of the actuators and the couple is a series of joints. The translation is in two axes: X and Y axes.
    %     \item \textbf{Coupler}
    %     \par
    %     This link transfers the motion to the output link: the rocker. Its design is shown in Figure \ref{fig:coupler}.
    %     \begin{figure}[H]
    %         \centering
    %         \includegraphics{Figures/KLink1.PNG}
    %         \caption{Coupler}
    %         \label{fig:coupler}
    %     \end{figure}
    %     The design is such that it hinges on an extension from the flap support frame on one end and connects to the rocker on the other end. The crank is connected at a distance from one end.
    %     \item \textbf{Rocker}
    %     \par
    %     The rocker connects to the coupler on one end and to the flap on the other end. Its design is as shown in figure \ref{fig:rocker}.
    %     \begin{figure}[H]
    %         \centering
    %         \includegraphics[height=.55\textheight]{Figures/KLink2.PNG}
    %         \caption{Rocker}
    %         \label{fig:rocker}
    %     \end{figure}
    % \end{enumerate}
    % \item \textbf{Discharge flow control sub-unit}
    % \par
    % In the assembly shown in Figure \ref{fig:flow_diversion_assembly}, the flap support frame hinges on two rods: one of the servo mount rods and the other is one of the legs of the electromagnetic holder.
    % \begin{figure}[H]
    %     \centering
    %     \includegraphics{Figures/DischargeFlowControlAssembly.PNG}
    %     \caption{Flow Diversion assembly}
    %     \label{fig:flow_diversion_assembly}
    % \end{figure}
    % \item \textbf{Finite element analysis of the electromagnetic actuator assembly}
    % \par
    % The finite element analysis of the assembly was performed to test how the electromagnetic diversion system is stable under a pressure force of $1N/m^{2}$ applied to the inside of the flap. PLA material was selected for all the parts in the assembly. The results of the simulation are shown in figure \ref{fig:e_simulation_results}.
    % \begin{figure}[H]
    %     \centering
    %     \includegraphics[height=\textheight, width=\textwidth]{Figures/DischargeFlowDiverSionAssembly-Static 1-1-1.png}
    %     \caption{Diversion assembly FEA results}
    %     \label{fig:e_simulation_results}
    % \end{figure}
    % From the results in figure \ref{fig:e_simulation_results}, it is evident that the electromagnetic actuator assembly holds up to the amount of distributed pressure on the flap. 
\end{enumerate}
\subsubsection{Electrical}
\begin{enumerate}
    \item \textbf{MG996R Servo motor connection}
    \par
    \begin{itemize}
        \item \textbf{Power requirements}
        \par
        From the technical specifications of the motor listed in table \ref{tab:MG996R_servo_specs}, this motor's operating voltage is 4.8V-7V, its driving current is between 500mA and 900mA, and its stall current is 2.5A(6V). However, most microcontrollers supply up to +5V DC voltage. This therefore requires a step-up circuitry or an external voltage supply to the  motor.
        \item \textbf{Connection}
        \par
        To connect an external supply requires a circuit shown in figure \ref{fig:servo_connection}.
        \begin{figure}[H]
            \centering
            
            \caption{Servo Connection}
            \label{fig:servo_connection}
        \end{figure}
        A 6V DC external supply is connected to the drain terminal of a Power MOSFET. This is activated by an NPN BJT transistor using the voltage supplied by the microcontroller.
    \end{itemize}
    
    \item \textbf{P16-S Electromagnetic Actuator connection}
    \par
    \begin{itemize}
        \item \textbf{Power requirement}
        \par
        The power requirements for this actuator are 12V DC supply and 2A current as listed in table \ref{tab:la_t8_tab}. These two power requirements cannot be satisfied by just a micro-controller; an external source is necessary.
        \item \textbf{Connection}
        \par
        This two power requirement can be satisfied using a combination of a MOSFET power IRF520 and a D1 flyback diode as shown in Figure \ref{fig:electromagnet_connection}.
        \begin{figure}[H]
            \centering
            
            \caption{Electromagnetic Actuator circuit}
            \label{fig:electromagnet_connection}
        \end{figure}
        This is available in a module shown in figure \ref{fig:irf520_module}.
        \begin{figure}[H]
            \centering
            
            \caption[IRF520 Module]{IRF520 Module \cite{irf520}}
            \label{fig:irf520_module}
        \end{figure}
    \end{itemize}
\end{enumerate}
\subsubsection{Software and control}

\begin{enumerate}
    \item \textbf{MG996R Servo motor control}
    \par
    \begin{itemize}
        \item \textbf{Requirements}
        \par
        This motor is required to drive the ball valve in steps in a $90^{0}$ turn, the angle covered to close and open the ball valve. However, the motor can turn $120^{0}$. Therefore, the $90^{0}$ turn can be achieved by Pulse Width Modulation. 
        \item \textbf{Control}
        \par
        From the motor's datasheet, the period of the motor's control signal is 50Hz(20ms). This is checked against the clock frequency of the microcontroller and used to determine the prescaler value for the timer register.
        \par
        For example:
        \begin{align*}
            \text{Consider a micro-controller with clock frequency:} 84MHz \\
            Timer\_Frequency = Period \times PWM\_Frequency\\
            \therefore = 20000 \times 50 Hz  = 1MHz\\
            Pre-scaler = \frac{Clock\_frequency}{Timer\_frequency}\\
            \therefore = \frac{84}{1} = 84
        \end{align*}
        The angle turned by the motor is proportional to the Logic HIGH duty. Therefore, by writing a time value for $90^{0}$ full turn in the timer register, the turn can be achieved. Smaller turns can be achieved by writing corresponding time values to the timer register.
    \end{itemize}
    \item \textbf{LA-T8 electromagnetic Actuator control}
    \par
    \begin{itemize}
        \item \textbf{Requirements}
        \par
        In order to divert the flow, this actuator is required to provide a linear stroke and remain in position for a set amount of time. When the time elapse, it is required to linearly retract in order to restore the flow. 
        \item \textbf{Control}
        \par
        This actuator provides a full length stroke in;
        \begin{align*}
            \text{Full length of a stroke: } = 100mm\\
            Stroke\_speed = 150mm/s\\
            \therefore \text{Time taken for a full length stroke is} \frac{10}{15}^{th}  \text{of a second.}
        \end{align*}
        This is achieved when it is powered. The terminals are switched in order to retract it.
        \par
        Shorter strokes can be achieved by turning on the actuator for a time less than $\frac{10}{15}$ \textit{th} seconds.
    \end{itemize}
\end{enumerate}
Controlling these two electronics requires an RTOS platform. There are many RTOS platforms but Zephyr and Mbed platforms are preferred because of their relatively large support with extensive APIs. 
\clearpage
\subsection{Discharge Handling Unit}
This unit consists of the following subunits:
\begin{enumerate}
    \item Discharge collection tank sub-unit.
    \item Outlet valve sub-unit.
    \item Weight measurement sub-unit.
    \item Temperature measurement sub-unit.
\end{enumerate}

\subsubsection{Discharge collection tank sub-unit}
\begin{itemize}
\item \textbf{Collection tank}
\par
This is used to temporarily collect the discharge from the pipeline during each step of an experiment, after which it is released to the main reservoir through an outlet valve. The weight and temperature of the discharge are also taken in this tank. 
\par
The following design considerations were made when selecting a tank for this application.
\begin{enumerate}
    \item Shape of the tank 
    \par
    The design of this tank should be such that the tank discharges in the least time possible with no remnants. Therefore, the shape of the tank was put into much consideration such that it influences/motivates the discharge. This consideration was made in tandem with the consideration of the position of the outlet valve.
    
    \item Material of the tank
    \par
    The collection tank will hold water with chlorine chemicals. This brings about the thread of rust. Therefore, the tank material was chosen so that it minimises this thread. 
    \item Volume of the tank
    \par
    The volume of the tank tank was such that it can hold a stream from the $1 \frac{3}{4} inch$ main discharge pipe that flows for approximately 30 seconds when the valve is fully opened. This was around $0.01m^{3}$. Therefore, the dimensions of the tank were such that it produced a volume of this value.
\end{enumerate}
Based on the above considerations, two options were technically feasible in terms of the available means for fabrication:
\begin{enumerate}
    \item \textbf{Cuboid tank}
    \par
    The design of the tank is shown in Figure \ref{fig:cuboid_discharge_container}.
    \begin{figure}[H]
        \centering
        
        \caption{Cuboid discharge container}
        \label{fig:cuboid_discharge_container}
    \end{figure}
    This tank satisfies the requirements for this application. However, a small volume of discharge will tend to remain in the tank when the tank is emptied.
    \item \textbf{Horizontal Cylindrical tank}
    \par
    The design of this tank is shown in Figure \ref{fig:horizontal_cylindrical_tank}.
    \begin{figure}[H]
        \centering
        
        \caption{Horizontal Cylindrical tank}
        \label{fig:horizontal_cylindrical_tank}
    \end{figure}
    When emptying this tank, the tank motivates the flow out of the discharge due to the concentration of the pressure of the discharge on a line at the bottom of the container determined by a static simulation.
    % \begin{figure}[H]
    %     \centering
    %     \includegraphics[width=\textwidth, height=.4\textheight]{Figures/tank-Static-1-1-1.png}
    %     \caption{Tank simulation results}
    %     \label{fig:tank_simulation_results}
    % \end{figure}
\end{enumerate}

The horizontal cylindrical tank was selected for this application.
\par
\item \textbf{Tank support frame}
\par
In order to support the tank in an upright position on a flat surface a support frame shown in figure \ref{fig:cylindrical_tank_support_frame}.

\begin{figure}[H]
    \centering
    
    \caption{Cylindrical tank support frame}
    \label{fig:cylindrical_tank_support_frame}
\end{figure}

The dimensions of the frame were such that it provides a clearance of 1mm for the tank.

\par
\item \textbf{Tank assembly}
\par
The assembly of the tank and its support frame are as shown in figure \ref{fig:collection_tank}.
\begin{figure}[H]
    \centering
    
    \caption{Collection tank}
    \label{fig:collection_tank}
\end{figure}
\par
\item \textbf{Position}
\par
The positioning of the tank was also a critical aspect of the design. Ideally, the collection tank was to be either positioned directly just below the flow diversion unit or at the periphery of the main reservoir. Positioning the collection tank directly below the flow diversion unit mitigates the need for additional components such as diverting pipes. This simply implies that the collection tank would just be provided with a holding mechanism for support upon which it is fitted with a solenoid outlet valve directly into the reservoir. On the contrary, positioning the collection tank on the periphery introduces the need for additional components. This includes a pump system to pump the discharge back into the reservoir, which adds to the overall cost of the project. Positioning the collection tank below the diversion unit was the feasible option.
\end{itemize}

\subsubsection{Outlet valve sub-unit}
This valve is attached to the collection tank and is used to empty the tank into the main reservoir. The main consideration was the response time(time taken to close and open the valve) in the selection of a valve suitable for this application. The following options were feasible:
\begin{enumerate}
    \item \textbf{An electrically Controlled Butterfly valve}
    \par
    \begin{figure}[H]
        \centering
        
        \caption[Butterfly valve]{Butterfly valve \cite{butterfly}}
        \label{fig:butterfly_valve}
    \end{figure}
    The operating voltage of the valve shown in figure \ref{fig:butterfly_valve} is in the range 12V DC - 230V AC. Therefore, its response time can be reduced by increasing the voltage supply to the solenoid.
    \item \textbf{A solenoid gate valve(with a plunger)}
    \par
    \begin{figure}[H]
        \centering
        
        \caption[Solenoid valve]{Solenoid valve \cite{solenoid}}
        \label{fig:solenoid_valve}
    \end{figure}
    The $\frac{3}{4} inch$ solenoid valve shown in figure \ref{fig:solenoid_valve} uses a plunger with a cork for control the flow. How fast the plunger closes the aperture depends on the voltage supplied to the solenoid. The operating voltage of this type of valve is 12V DC.
\end{enumerate}

The solenoid gate valve(with a plunger) was selected for this application mainly because the butterfly valve is expensive relative to the budget set for the project.

\subsubsection{Weight measurement sub-unit}
The weight of the collected discharge is measured in every step in an experiment done on this machine. The weight can be cumulative or measured per step. In the event of an error, the error is not propagated in the cumulative approach, but it will definitely be propagated to every measurement in the weight-per-step approach. Therefore, the weight-per-step approach was selected for this application.
\par
During the selection of a method to use for weight measurement of the discharge, the following considerations were made:
\begin{enumerate}
    \item The maximum weight that can be precisely measured by the unit. The maximum weight of the structure to be measured is determined as follows:\\
    \begin{align*}
    \text{Assume the maximum volume of the water collected} = 0.02m^{3}.\\
    Mass(M) = Density(\rho) \times Volume(V)\\
    \text{Water density} (\rho_{\textit{water}}) = 1000kg/m^{3}\\
    \therefore  \text{Mass of water} (M_{\textit{water}}) = 20 Kg
    \end{align*}
    The measuring device should therefore handle weights of more than 20Kg.
    \item The resolution of the device.
    \item The credibility of the weight measurement device.
\end{enumerate}
On the basis of the above considerations, the following options were considered:
\begin{enumerate}
    \item Weight measurement by ultrasonic waves
    \par
    Ultrasonic waves can be used to determine the depth of discharge in the tank. An ultrasonic wave generator generates an ultrasonic wave and is propagated to the surface of the water. It is then reflected due to refraction to a receiver. The time taken to send and receive the echo is multiplied by the speed of sound to obtain the depth of the empty side of the container. \par 
    This approach is rudimentary and very much flawed as there are many considerations in order to obtain almost accurate results. Some of the considerations include:
    \begin{enumerate}
        \item The angle of reflexion $\delta$ is shown in figure \ref{fig:ultrasonic sensor measurement model}.
        \begin{figure}[H]
            \centering
            
            \caption[Ultrasonic sensor measurement model]{Ultrasonic sensor measurement model \cite{chang1996ultrasonic}}
            \label{fig:ultrasonic sensor measurement model}
        \end{figure}
        \item The Gaussian noise to environmental changes. There is an almost 3.5\% increase in noise for a temperature difference of only $20^{0}$ \cite{chang1996ultrasonic}.
    \end{enumerate}
    To use this approach requires calibration of many parameters, some of which are to be done in real time. A mathematical model would be preferable for this calibrations.
    \item Load cells
    \par
    These are transducers capable of converting pressure to an electrical signal specifically a strain in its material structure is converted to electrical resistance.
    \par
    The loading cell disc shown in Figure \ref{fig:load_cell_disc} with a load force range of 0-50Kg was selected for application due to its weight range.
    \begin{figure}[H]
        \centering
        
        \caption[Strain-type load cells]{Strain-type load cells \cite{loadcell}}
        \label{fig:load_cell_disc}
    \end{figure}
\end{enumerate}
The use of a load cell was selected for this application based on the merits listed in the descriptions above. However, a single-load cell disc will be inefficient in measuring the weight of this load. Therefore, four load cells selected were strategically positioned at the edges of the support frame of the discharge collection tank, as shown in Figure \ref{fig:collection_tank_with_load_cells}.
\begin{figure}[H]
    \centering
    
    \caption{Collection tank with load cells}
    \label{fig:collection_tank_with_load_cells}
\end{figure}

\subsubsection{Temperature measurement sub-unit}
In the same way as weight measurement of the discharge, the temperature of the discharge is measure in every step. This is relevant in ensuring consistency of the data collected in an experiment done in this machine. Since this measurement is taken within roughly 10 seconds before the outlet valve is opened, a measuring device whose sensitivity is enough to establish reliable results within that time is required for this application. A couple of temperature measurement sensors were considered for this application but an immersible DS18B20 temperature probe shown in figure \ref{fig:ds18b20_temperature} was selected. Its technical specifications are shown in table \ref{tab:ds18b20 temperature probe}.
\begin{figure}[H]
    \centering
    
    \caption[DS18B20 temperature probe]{DS18B20 temperature probe \cite{ds18b20}}
    \label{fig:ds18b20_temperature}
\end{figure}
\begin{table}[H]
\centering
\caption[DS18B20 temperature range specifications]{DS18B20 temperature range specifications \cite{ds18b20}}
\begin{tabular}{|l|l|}
\hline
\textbf{Property} & \textbf{Value} \\ \hline
Operating voltage & 3.3V  to 5V DC \\ \hline
Operating temperature range & -55°C to +125°C (-67°F to +257°F) \\ \hline
Accuracy over the range of -10°C to +85°C: & ±0.5°C. \\ \hline
Water proof & True \\ \hline
\end{tabular}
\label{tab:ds18b20 temperature probe}
\end{table}

\subsubsection{Electrical}
\begin{enumerate}
    \item \textbf{Solenoid valve connection}
    \par
    \begin{itemize}
        \item \textbf{Power requirements}
        \par
        The selected solenoid valve operates on 12V DC voltage. This requires an external supply and circuit to activate the supply when needed.
        \item \textbf{Circuit}
        \par
        An IRF520 N-Ch power module described previously can be used to power this device with a 12V supply.
    \end{itemize}
    \item \textbf{Strain type load cell connection}
    \par
    \begin{itemize}
        \item \textbf{Power requirements}
        \par
        The four load cells used in this application are connected through a load combinator module whose operating voltage is between 2.7V to 5V.
        \item \textbf{Circuit}
        \par
        The load cells are connected in a Wheat-stone bridge through a load combinator module as shown in figure \ref{fig:load_cell_circuit}.
        \begin{figure}[H]
            \centering
            
            \caption[Load cells circuit]{Load cells circuit \cite{loadcell}}
            \label{fig:load_cell_circuit}
        \end{figure}
    \end{itemize}
    \item \textbf{DS18B20 temperature probe connection}
    \par
    \begin{itemize}
        \item \textbf{Power requirements}
        \par
        This sensor's operating voltage is between 3.0V and 5V. Therefore Vcc line can be connected directly to the 5V pin of the micro-controller.
    \end{itemize}
\end{enumerate}
\subsubsection{Software and control}
\begin{itemize}
    \item \textbf{Calibration}
    \par
    The load cells and the temperature sensor are calibrated once the whole system is assembled.
    \item \textbf{Auto calibration}
    \par 
    This can be achieved by having weight and temperature measurements triggered by an event and only measuring differential values.
    \item \textbf{Mean}
    \par
    In this application, the weight and temperature of the discharge is measured over a period of time before the value of a measurement is determined. The noise in the variation within that time can be minimized by using a calibrated Kalman's filter.
\end{itemize}

\subsection{Interface and Control Unit}
This unit consists of two subunits:
\begin{enumerate}
    \item Interface sub-unit
    \item Controller sub-unit
\end{enumerate}

\subsubsection{Interface sub-unit}
It provides for a means of interaction between the system and the user. Ideally, the sub unit enables the user to input instructions and control the processes in this system. The status and results of processes in this system are also displayed in the interface. The choice of an interface depended on the following factors:
\begin{enumerate}
    \item Size \\
    This is the size of the operable part of the interface. In case of touch interface, a minimum of a 320x240 LCD is required to enable at least the minimum operability of GUI items, and a 20x4 LCD for any other choice.
    \item Ergonomics \\
    This refers to the impact of the interface on the user, the ease and efficiency in operating it. For an interface for this application, the user should be able to spend the least possible time feeding input and reading the results with relative ease. 
    \item Aesthetics \\
    This is the perception of the user while operating the interface, their feeling about the interface. For this application, the interface will be used most frequently by students with limited exposure. A good look might be motivating. However, this should not compromise the design. It should be able to be introduced and improved with minimum modifications to the hardware in the system. 
\end{enumerate}
Based on the above considerations, the following options were considered:
\begin{enumerate}
    \item LCD With keypad 
    \par
    This type of interface is shown in figure \ref{fig:lcd_with keypad}. One can navigate, read and provide input where it is required on the LCD display using the keypad.
    \begin{figure}[H]
        \centering
        
        \caption[LCD with keypad]{LCD with keypad \cite{lcd_with_keypad}}
        \label{fig:lcd_with keypad}
    \end{figure}
    \item LCD with touch 
    \par
    This type of interface is shown in figure \ref{fig:lcd_with_touch}. One can navigate such interface easily by touching or use a virtual keyboard to provide input. 
    \begin{figure}[H]
        \centering
        
        \caption[LCD with touch]{LCD with touch \cite{lcd_with_touch}}
        \label{fig:lcd_with_touch}
    \end{figure}
     This type of LCD communicates with the microcontroller through an 8-bit parallel interface and four ports(32 pins). This can sometimes be replaced by an HDMI interface depending on the size of the screen.
    \item LCD with Knob
    \par
    This interface shown in Figure \ref{fig:lcd_with_knobs} is controlled by a knob. Navigation from page to page,field to field is achieved by turning the knob. To provide an input in a field, the knob can be pressed and turned. This is common in low-budget 3D printers.
    \begin{figure}[H]
        \centering
        
        \caption[Lcd with knob]{LCD with knob \cite{noauthor_prusa_nodate}}
        \label{fig:lcd_with_knobs}
    \end{figure}
\end{enumerate}

 An efficient choice for this application was to use a touch LCD interface. This choice satisfies all the requirements required of an interface for this application. In addition, one can also improve the aesthetics of the design by simply tweaking the GUI software without major hardware changes.
 \par
 Touch LCDs can be very expensive relative to our budget and challenging to programme. Two variations of touch LCDs are available for our application: those with a 32-pin interface and those with an HDMI interface. Those with HDMI interface are available in sizes larger than 7 inches and are priced at not less than \$90. Those with 32-pin interface are available to sizes as small as 1.77 inches and are relatively cheaper.    
\begin{itemize}
    \item \textbf{LCD GUI design}
    \par
    A preliminary GUI is shown in Figure \ref{fig:GUI_interface}.
    \begin{figure}[H]
        \centering
        
        \caption{GUI interface}
        \label{fig:GUI_interface}
    \end{figure}
    The design is in a 320x240 frame, the size of the selected LCD. The steps sizes and time interval's inputs can be provided by sliding on the sliding bar. The value of a position on the slider is displayed on a label beside the sliding bar. The step number, weight and temperature of that specific step are also displayed once a step is complete.
    Finally, in case of any errors in the system, an error message is displayed at the bottom of the frame.
\end{itemize}

\subsubsection{Controller sub-unit}
This sub-unit executes the application logic, sends instructions to the actuators, and reads inputs from sensors in the system. It is responsible for synchronising the GUI with the processes in the hardware. This unit monitors and controls the parameters of the input devices and generates output signals to implement desired tasks.
\par
The choice of a micro-controller for this application was guided by the selected interface, a touch LCD. Figure \ref{fig:mcu selection} shows the selection procedure for a micro-controller for this application.

\begin{figure}[H]
    \centering
    
    \caption{Board Selection}
    \label{fig:mcu selection}
\end{figure}

\begin{itemize}
    \item \textbf{Graphics library} 
    \par
    To develop graphics for a touch LCD, the choice of graphics libraries was between the Light and Versatile Embedded Graphics Library (LVGL) and the Qt/QML graphics libraries. These two are versatile and have great community support. Each library supports specific display drivers out-of-the-box. For this application, an LCD with an ILI9341 driver had been selected, therefore support for this specific driver was necessary. Drivers for a specific driver could also be developed from scratch in a long and tedious process. To avoid this, out-of-the-box support was required. LVGL tends to offer that support; therefore, it was selected as the graphics library for this application.
    \item \textbf{Board support} 
    \par
    LVGL library also provides support for specific board families out of the box, such as the NXP and STM32F4 families. LVGL support for these boards automatically means that this board has the number of ports required for LCD touch functionality.
    \item \textbf{Platform support}
    \par
    LVGL is just a graphics library. The board is required to support other peripherals such as the electromagnet, servo motor, weight and temperature measurement devices, and the solenoid valve. This can be done in an RTOS platform such Zephyr(C/C++) or Mbed(C++). However, these platforms support specific boards out-of-the-box, but custom boards could also be added. To make the project a little easier, an out-of-the-box was required. The two platforms tend to support the two boards. 
    \item \textbf{Price}
    \par
    This is the most crucial part of this selection. Both boards can be considered expensive relative to the project's budget, but the STM32F4 family boards can be relatively cheaper. Therefore, an STM32F407VET6 board was selected.
\end{itemize}

\subsubsection{Electrical}
\begin{itemize}
    \item \textbf{Touch LCD connection}
    \par
    STM32F407VET6 board provides a dedicated interface for touch LCD with FSMC interface as shown in figure \ref{fig:fsmc_interface}.
    \begin{figure}[H]
        \centering
        
        \caption[Load cells circuit]{FSMC interface in STM32F407VET6 \cite{mcu_lcd}}
        
        \caption[STM32 connected with LCD]{STM32 connected with LCD \cite{mcu_lcd}}
        \label{fig:fsmc_interface}
    \end{figure}
\end{itemize}

\subsubsection{Software and control}
The logic of the whole application is shown in figure \ref{fig:application_logic}.

\begin{figure}[H]
    \centering
    
    \caption{Application logic}
    \label{fig:application_logic}
\end{figure}

The application requires the user to set the number of steps of the experiment or the time interval between the steps. This is done by sliding the slide handle of one of the inputs in the touch GUI. When the user presses the handle on the input of the steps, the system automatically adjusts the time interval between the steps and vice versa. Once the steps are set, the user clicks on the start button. The system then turns the valve by one step after starting the timer. This is done simultaneously with commencement of the discharge collection and the measurement of the discharge temperature.
\par
The system will continuously check if the time interval has elapsed and if it has, it will simultaneously stop the discharge collection and the temperature measurement.  It will then compute the differential change in temperature and measure the weight of the discharge. The results of this measurement are displayed in the GUI. The process is repeated for the set steps but the user has the option to cancel the experiment.

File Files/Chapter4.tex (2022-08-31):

\section{Results}
This section contains the results obtained during the design process of the whole the project.
\subsection{Discharge Flow Control Unit}
\subsubsection{Flow control sub-unit}
An MG996R servo motor was selected for this sub-unit, to open and close the valve in steps that can be less than $1^{0}$ depending on the number of steps requested by the user. Direct pulse width modulation was preferred to a micro-step drive as a mechanism to drive the servo motor in steps of any size.
\par
A mounting mechanism for the servo motor was designed to the specifications of the motor and finite element analysis conducted as shown in figure \ref{fig:servo_assembly_results} .   
\begin{figure}[H]
      \centering
         
          \caption{Servo Assembly simulation results}
          \label{fig:servo_assembly_results}
      \end{figure}
    The interface and the servo mounting rods were subjected to stress analysis. With the axis of rotation symmetrical to the motor cage, the components were subjected to a torque of 1.176798N/m which is the maximum torque produced by the stepper motor. The serrated strap and the servo motor cage are found to withstand the maximum torque of the servo motor an indication of low mechanical stress experienced by the components. However, the interface and the servo motor mounting rods are seen to undergo minimal deflections from the same torque. The deflections, however,is not significant enough to a point of failure. 
\subsubsection{Flow diversion sub-unit}
A LA-T8 micro-linear actuator with a linear stroke length of 100mm and stroke-speed of 150mm/s was selected to operate a flap used to divert the discharge flow either into the main reservoir or the discharge collection tank.A rocker link, was designed and simulated in MechDesigner software based on the motion required for the flap. The chain achieved the motion based on the cam data obtained from the simulation.
\begin{figure}[H]
         \centering
         
         \caption{Flow Diversion assembly}
         \label{fig:flow_diversion_assembly}
     \end{figure}
\par
Flow diversion assembly in conjunction with the flow control unit unit not only precisely controls the flow rate from the pipeline but also the discharge into the collecting tank or into the main reservoir. The linear motion of the actuator which is connected to the flap by mean of a rocker link achieves this function. A motion study simulation was conducted in SolidWorks. From  the study, in every step turn of the servo motor, the system effectively diverts the discharge to either into the collection tank or the main reservoir. 
\subsubsection{Discharge flow control Unit Assembly}
The assembly of the discharge flow control unit is shown in figure \ref{fig:unit_exploded_view}.
\begin{figure}[H]
    \centering
    
    \caption{2D Wireframe Model of the Final Assembly}
    \label{fig:final assembly}
\end {figure}
The exploded view of this unit is shown in figure \ref{fig:unit_exploded_view}.
\begin{figure}[H]
    \centering
    
    \caption{Unit Exploded view}
    \label{fig:unit_exploded_view}
\end{figure}
From a motion study simulation in SolidWorks, the assembly appears to be able to regulate the fluid flow in steps as per the user's specifications. The diversion unit also seems to be able to divert the flow either to the main reservoir or to the discharge collection tank.

\subsection{Discharge Flow Handling unit}
\subsubsection{Discharge collection tank sub-unit}
The horizontal cylindrical tank selected for discharge collection process was subjected to a stress test of 1 Pascal. This was essential to determine the stress distribution in the whole tank tank system when fully filled with the discharge. This was essential in order to minimize the time taken to empty the tank. The results of the simulation is as shown in figure \ref{fig:tank_simulation_results}
  \begin{figure}[H]
         \centering
         
         \caption{Tank simulation results}
         \label{fig:tank_simulation_results}
     \end{figure}
\par
From the simulation, the pressure in the tank was mostly concentrated at the sides close to the lower bottom line of the tank. The collected discharge will thus apply the same pressure on the tank and with the tap at the bottom, less time will be taken to empty the tank.
% \subsubsection{Outlet valve sub-unit}
% A solenoid valve was preferred to a butterfly valve because of its relatively cheaper price though the preferred size is slower.
% \subsubsection{Weight measurement sub-unit}
% Four load cells connected on a Wheatstone bridge were preferred to an ultrasonic approach to measure the weight of the collected discharge because the ultrasonic approach is unreliable.
% \subsubsection{Temperature measurement sub-unit}
% A DS18B20 immersible temperature sensor was selected for this subunit due to its reliability and sensitivity.
% \par
\subsubsection{Final assembly}
Figure \ref{fig:final assembly} shows the designed system attached to the Synthetic Hydro-Experimental Machine currently in use in JKUAT. The unit is designed as a plug-and-play plugin, in that it is not permanently fixed onto the machine but can  be removed. This is so as to ensure the machine can be used to perform other experiments.
\begin{figure}[H]
    \centering
    
    \caption{Final Assembly with detailed view}
    \label{fig:final assembly}
\end{figure}
 The dimensions of the body are derived from the existing machine.
 \subsection{Full electrical circuit}
Figure \ref{fig:electrical_assembly} shows the electrical circuits of the two electronics: MG996R Servo motor and an LA-T8 Micro-linear actuator combined and simulated. The circuit uses a single external power supply from a 220V AC to 12V DC transformer. This is connected directly to the LA-T8 power circuit, and a regulator is used to step down the 12v to 6V for the MG996R stepper motor power circuit.
 \begin{figure}[H]
     \centering
     
     \caption{Electrical assembly}
     \label{fig:electrical_assembly}
 \end{figure}

\subsection{Budget}
The table \ref{tab:budget} shows the budget of the project.
\begin{table}[H]
\centering
\caption{Budget}
\label{tab:budget}
\resizebox{\columnwidth}{!}{%
\begin{tabular}{|l|l|l|l|l|l|}
\hline
\textbf{Item No.} & \textbf{Item} & \textbf{Description} & \textbf{Unit Cost} & \textbf{No.} & \textbf{Total Cost} \\ \hline
1 & Servo Motor & MG996R(4.8Kg/cm) & 800 & 1 & 800 \\ \hline
2 & Linear Actuator & LA-T8 Linear Actuator & 3500 & 1 & 3500 \\ \hline
3 & Load cells & 50 Kg Load cells & 150 & 4 & 600 \\ \hline
4 & Load cell Amplifier & HX711 & 100 & 1 & 100 \\ \hline
5 & Temperature Sensor & DS18B20 Immersible & 300 & 1 & 300 \\ \hline
6 & Solenoid valve & 3/4''  Plastic & 900 & 1 & 900 \\ \hline
7 & MCU & STM32F407VET6 & 4400 & 1 & 4400 \\ \hline
8 & LCD & 320x240 Touch LCD & 1200 & 1 & 1200 \\ \hline
9 & Power MOSFET & IRF520 N-ch & 550 & 3 & 1650 \\ \hline
10 & Voltage Regulator & XL4015 DC-DC adjustable buck module & 400 & 3 & 1200 \\ \hline
11 & Transformer & AC 220V TO DC 12V 5A Transformer Power Supply & 1100 & 1 & 1100 \\ \hline
12 & Fabrication Cost & 3D printing \& Others & 10000 & 1 & 10000 \\ \hline
Total &  &  &  &  & \textbf{22600} \\ \hline
\end{tabular}%
}
\end{table}

    Some of the components such as LA-T8 micro-linear actuator, and the MCU with LCD,  are not available locally. The price indicated in the budget has their shipping cost included.
    Components such as strain-type load cells goes for Ksh. 250 a piece in Kenya. A temporary good deal was found on AliExpress, that reduced the price by half. The same case applied to the MCU board with the LCD. The fabrication cost indicated in the budget is the maximum possible estimate.

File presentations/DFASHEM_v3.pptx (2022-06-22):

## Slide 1

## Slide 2

Presentation Outline

- Abstract
- Introduction
Background, Problem Statement, Objectives, Justification
- Literature Review
  - Existing Technologies
  - Related Works
  - Gaps
- Proposed Methodology
- Expected outcomes
- Proposed Budget and Time plan

## Synthetic Hydro-Experimental Machine

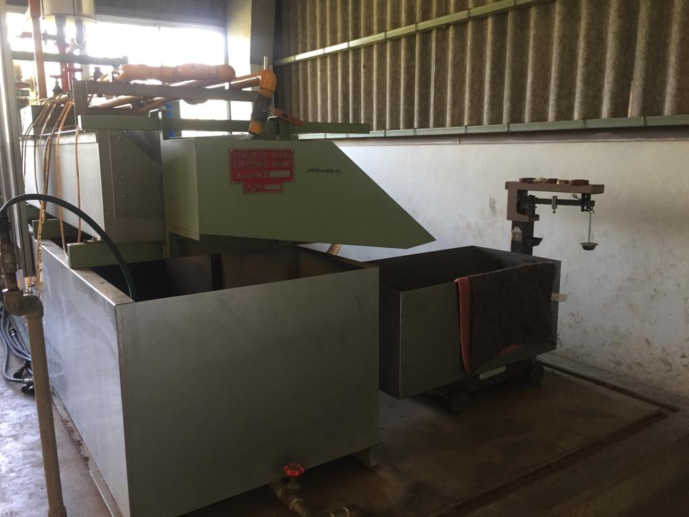
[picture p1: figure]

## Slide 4

Introduction: Background

- Fluid flow measurement
    - Quantifying a property of an uninterrupted flow.
- Flow meters
    - Turbine flow meter, rotameter, venturi, and orifice.
    - Bernoulli’s Theorem.
- Synthetic Hydro-Experimental Machine
    - Consists of venturi, and orifice
    - Establishing a relationship between discharge, differential pressure, and the coefficient of discharge.
    - Experiment procedure

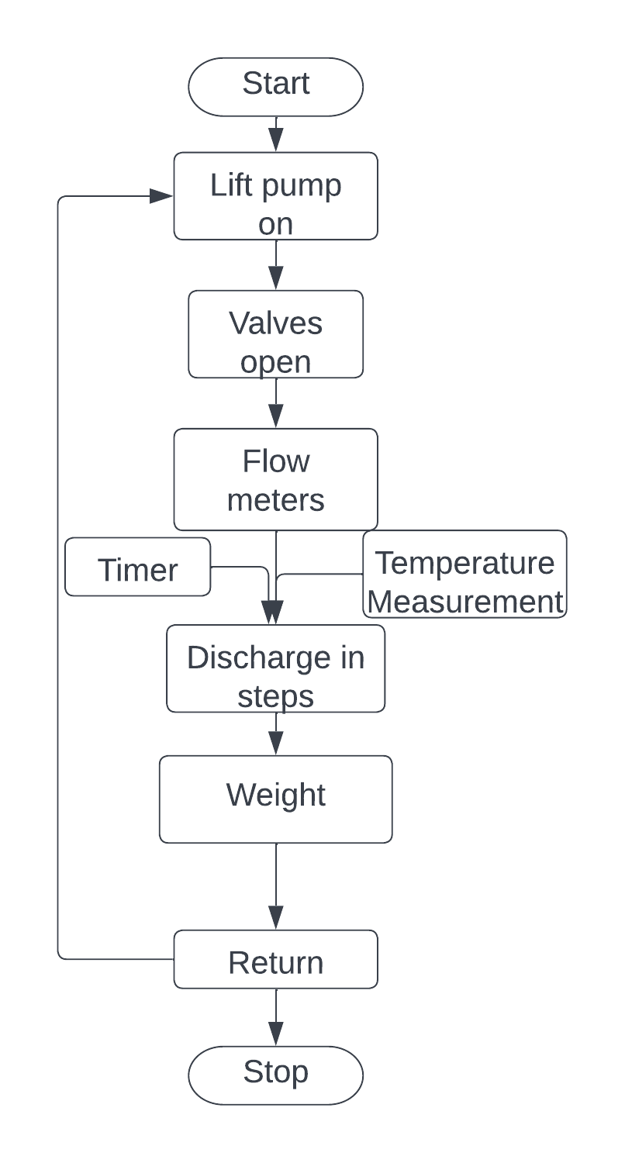
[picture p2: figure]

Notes: Fluid flow property measured and related to the flow. (relating pressure to the flow)
Each flow meter alter a physical property and the measures the change.
Bernoulli’s theorem – an increase in the velocity of a fluid occurs simultanously with a decrease in static pressure.
Procedure

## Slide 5

Introduction: Problem Statement

- Fluid flow experiments required one to synchronize discharge collection with time and temperature measurement.
- Current state of the Synthetic Hydro-Experimental Machine.
      - Determination of steps based on human intuition
      - Discharge collection synchronization by a minimum of two operators
      - Incremental weight measurement.
      - Results in Cd outside the tolerable range.
- Automated Synthetic Hydro-Experimental Machine
      - Precise discharge flow control.
      - Automated discharge collection.
      - Automate discharge weight and temperature measurement.

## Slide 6

Introduction: Objectives

Main Objective
To automate the discharge collection process of the Synthetic Hydro-Experimental Machine.

Specific Objectives
  1. To design an automated discharge flow control unit that can precisely discharge in steps.
  2. To design and fabricate a discharge collection unit with automated weight, time and temperature measurements.
  3. To design a user interface and the control algorithm.

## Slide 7

Literature Review: Existing technologies

Computational Fluid Dynamics
- Powerful modeling and analysis technique of non-linear differential equation of fluid flow properties.
- Tukimin et al developed a CFD model to determine the coefficient of discharge of the Venturi. They compared the results to those obtained from a physical experimental setup.
- The results showed a 1% difference.
Analytical Predictions
- Utilizes Bernoulli’s equation.
- Assumptions - Flow is linear.
- Flow is incompressible.
- The flow is steady
- No losses.

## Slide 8

Literature Review: Related Works

Electromagnetic Activation
- Automated Water Sampler
Angelo et al
Water sample collection
- Actuation mechanism >
Pneumatics
  - Power of compressed air for actuation
Sangmin and Joonwon
- Dispensing doses

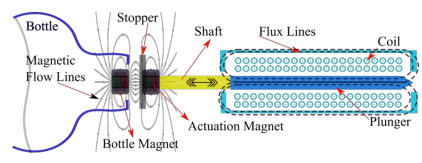
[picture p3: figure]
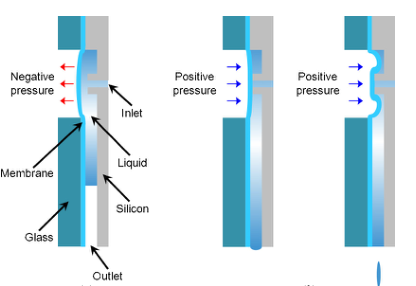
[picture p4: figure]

## Literature Review: Gap Analysis

- CFD
- undermines credibility of the experiment.
- Computational resource intensive (ANSYS).
- Analytical
- Tedious computations
- Assumptions
- Synthetic Hydro-Experimental Machine.
- Mechanical and manual.

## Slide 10

Methodology: Discharge Flow Control

Requirement: Discharge in precise steps
- Utilizes the existing ball valve.
Actuation Mechanisms
- Stepper Linear Actuator
- Piezoelectric Actuator
Considerations
- Torque requirements
- Step size

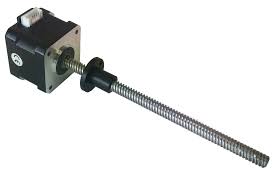
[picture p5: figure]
Linear Stepper Motor Nema 17 External, screw 8x8mm-150mm - SOPROLEC
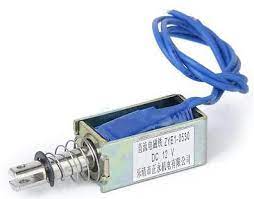
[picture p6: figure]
Electromagnetic Actuators

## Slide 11

Methodology: Discharge Flow Control

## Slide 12

Methodology: Dischare collection unit

- Flow Diversion Sub-unit
Requirements: - Fast response
- Minimal Splashes
Consist of a flap and an actuation mechanism.
Considerations: Size, shape, material
Actuation mechanisms: Motor, electromagnets.
- Discharge collection tank
Requirements: - elevation utilizes gravity
- Minimal environmental effect.
Considerations: - Position
- Insulation
- Shape

- Outlet valve.
Requirement: faster discharge
Considerations: Position and size.
  - Weight Measurement
Approaches: Ultrasonic, Load cells
Considerations: Reliability
    - Temperature measurement
Approaches: Contact and non contact
Considerations: - Sensitivity.
- Reliability.

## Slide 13

Methodology: Interface and Control

- Processing Unit.
    - GPIOs
    - Processing power
- Interface.
    - Ergonomics.
    - Size.
    - Aesthetics.

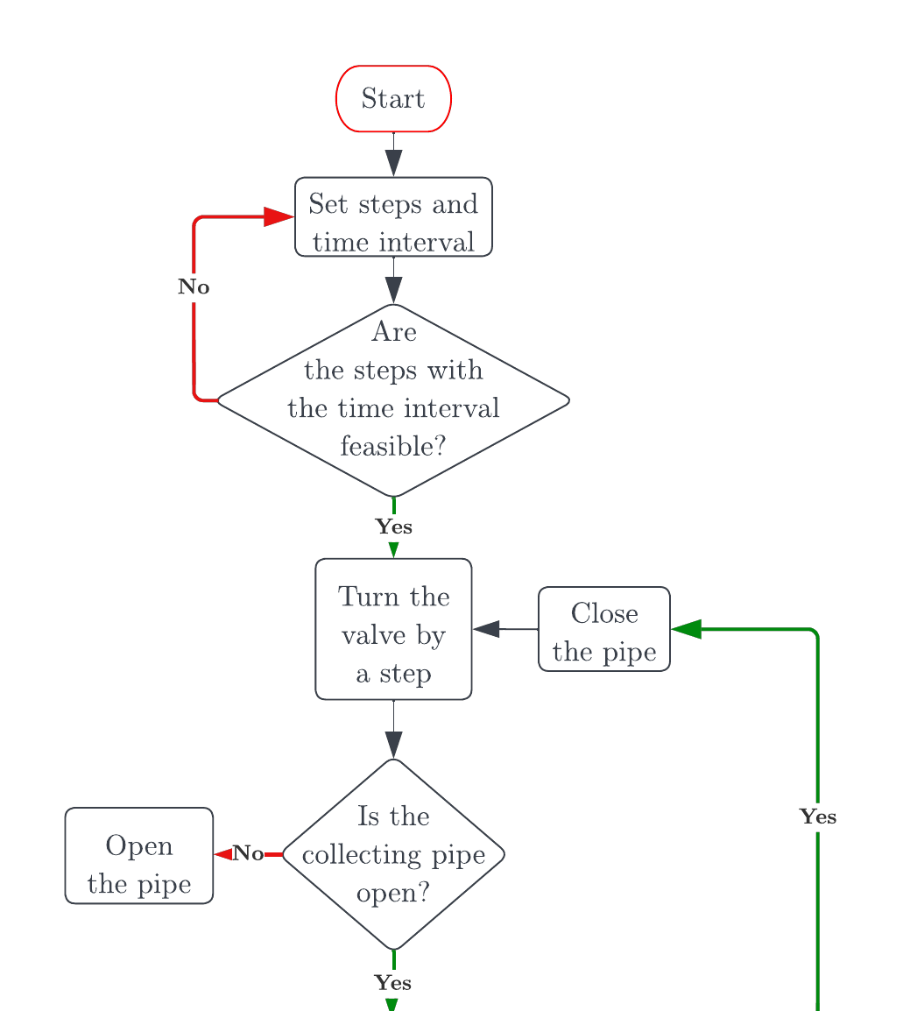
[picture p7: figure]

## Methodology: Control Cont…

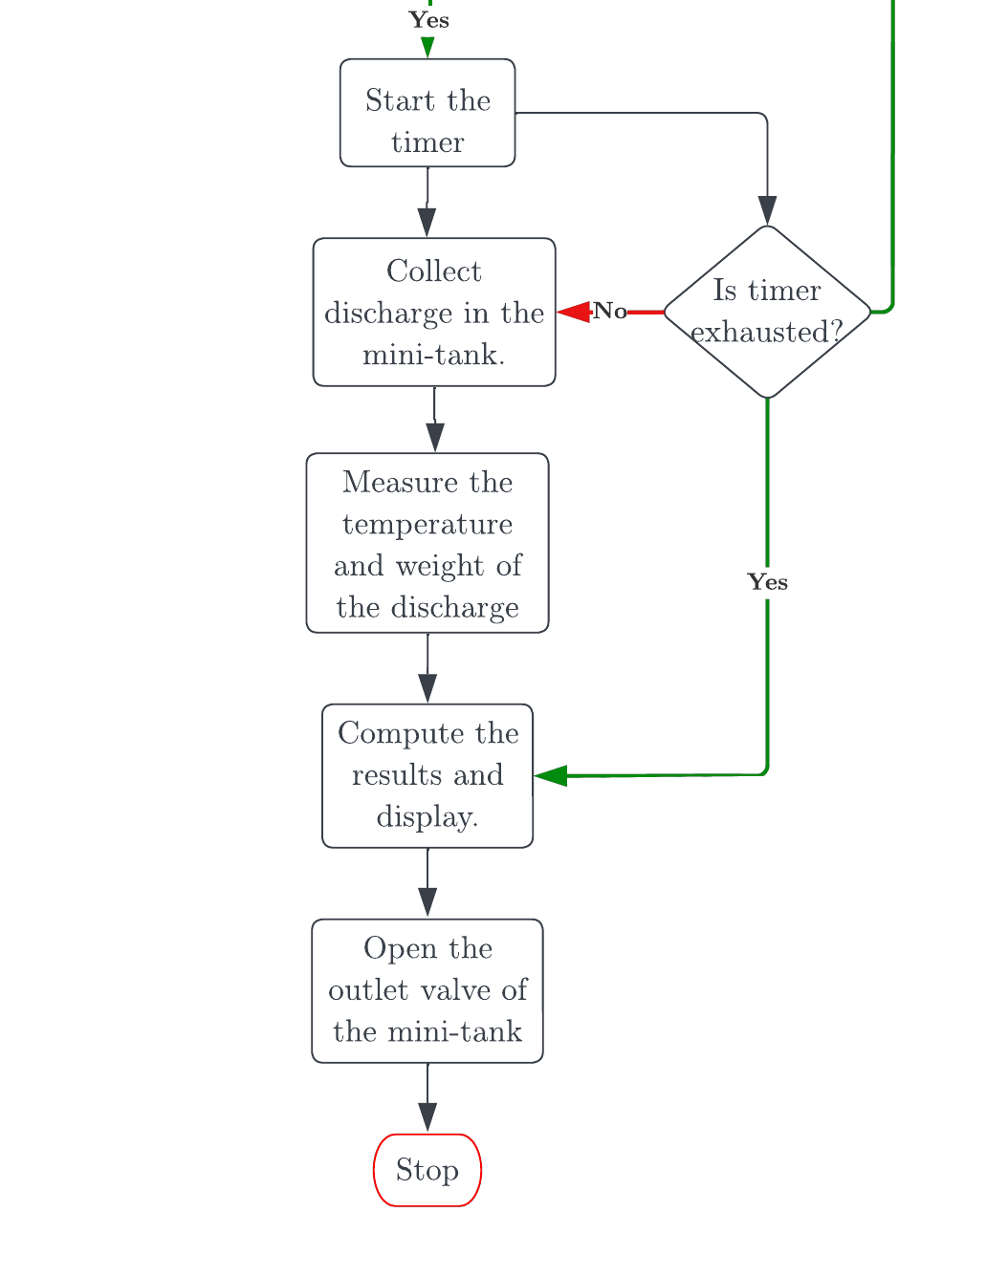
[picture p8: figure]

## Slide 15

Expected Outcomes

- Discharge flow control
- Can turn the ball valve in precise steps.
- Accuracy of the steps is to the nearest whole number.
- Discharge collection unit
- Synchronized discharge collection with temperature and weight measurements.
- Flow diversion unit
- Accurate collection of the stream within the time interval.
- Discharge collection tank.
- Correctly shaped for accurate weight measurement.
- Utilize gravity to eliminate the need for an extra pump.
- Control and display
- Ergonomic Display
- Capable board

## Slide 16

Time plan

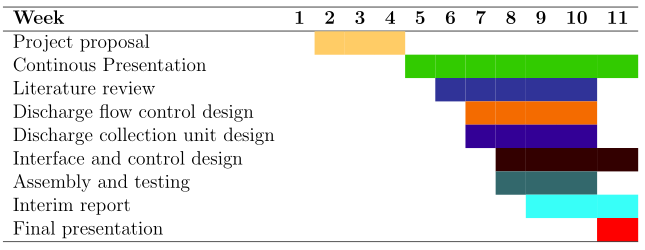
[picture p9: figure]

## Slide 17

Budget

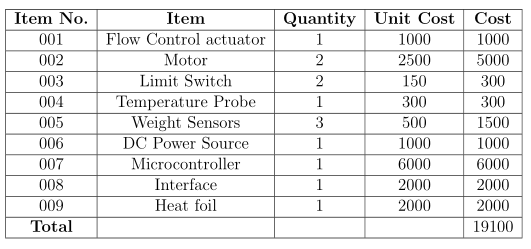
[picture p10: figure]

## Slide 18

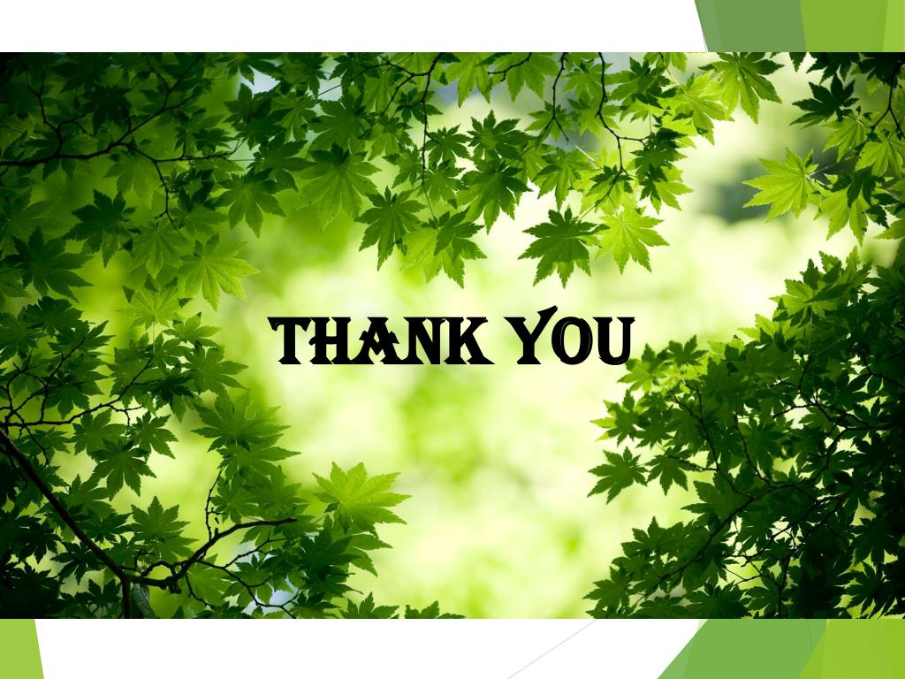
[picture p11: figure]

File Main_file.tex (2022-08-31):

\documentclass[12pt,fleqn]{article}
\usepackage{a4}
\usepackage{graphicx}
\usepackage[table,xcdraw]{xcolor}
\graphicspath{ {./Figures/} }
\usepackage{psfrag}
\usepackage{amsmath}                     % \boldsymbol{#1}
\usepackage{amssymb}
\usepackage{Styles/hangcaption}
\usepackage{pstricks}
\usepackage{Styles/pst-node}
\usepackage{Styles/fancyheadings}
\usepackage{tocloft}
\usepackage{cite}
\usepackage{hyperref}
\usepackage[printonlyused]{acronym}
\usepackage{epstopdf}
\usepackage{datetime}
\usepackage{pdfpages}
\usepackage{tabulary}
\usepackage{longtable}
\usepackage[table,xcdraw]{xcolor}
\usepackage{lscape}
\usepackage{float}

\usepackage{capt-of}
\usepackage{array}
\usepackage{colortbl}
\usepackage{rotating}

\newdateformat{monthyeardate}{%
\monthname[\THEMONTH], \THEYEAR}
\hypersetup{
    colorlinks=false,
    linkcolor=black,
    filecolor=black,      
    urlcolor=black,
    }
    
\usepackage{nomencl}
\makenomenclature

\newcommand\Nomenclature[2]{\nomenclature[#2]{#1}{#2}}

% \newcommand{\yesthreeday}{{\AdvanceDate[-4]\today}}
\epstopdfDeclareGraphicsRule{.pdf}{png}{.png}{convert #1\OutputFile}
\DeclareGraphicsExtensions{.png,.pdf}

%-----Tex width---------------------------------
\textwidth 16cm

%-----Line spacing-------------------------------
\renewcommand{\baselinestretch}{1.5}     % 1,1-zeilig

%---------Add dots in TOC-----------------------
\renewcommand{\cftsecleader}{\cftdotfill{\cftdotsep}}

%------Paragraph indention-------------------------------
\setlength{\parskip}{1.5ex plus0.5ex minus0.5ex}

%-----Prevent indent----------------------
\setlength{\parindent}{0em}

%-----Richtiger Abstand fur Einheiten-------------
\def\Unit{\hspace{0.25em}}

%-----Definition of the header--------------------
\pagestyle{fancyplain}
\renewcommand{\sectionmark}[1]{\markboth{Chapter~\thesection.~#1}{#1}}
\renewcommand{\subsectionmark}[1]{\markright{\thesubsection\ #1}}
\rhead[\fancyplain{}{\leftmark}]%
{\fancyplain{\thepage}{\thepage}} \cfoot{} \plainheadrulewidth
0.4pt

\makeatletter
\ifcase \@ptsize \relax % 10pt
  \addtolength{\headheight}{1\p@}
\or % 11pt
  \addtolength{\headheight}{2\p@}
\or % 12pt
  \addtolength{\headheight}{3\p@}
\fi \makeatother

%-----Equations / Figures / Tables numbering according to \ sections
\makeatletter
\renewcommand\theequation{\thesection.\arabic{equation}}
\renewcommand\thefigure{\thesection.\arabic{figure}}
\renewcommand\thetable{\thesection.\arabic{table}}
\@addtoreset{equation}{section} \@addtoreset{figure}{section}
\@addtoreset{table}{section} \makeatother

%-----Useful abbreviations----------------------
\newcommand{\mr}{\mathrm}
\newcommand{\bs}[1]{\mbox{$\boldsymbol{#1}$}}
\newcommand{\degree}[1]{\mbox{$#1^\circ$}}

%------Bibliography style-----------------------
\bibliographystyle{IEEEtran}

%-----Aufzaehlunstiefe im Literaturverzeichnis---------------
\setcounter{tocdepth}{3}

\begin{document}
\pagenumbering{Roman}
\begin{titlepage}
  \begin{center}
      \vspace*{-4.0cm}
    \begin{figure}[!h]
\centering
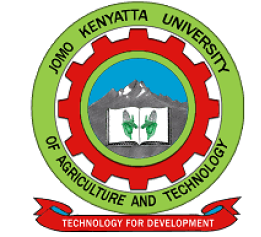
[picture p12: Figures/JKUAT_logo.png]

\label{fig:jomologo}
\end{figure}
   \large{Jomo Kenyatta University of Agriculture and Technology}\\
    \large{College of Engineering and Technology}\\
    \large{School of Mechanical, Materials, and Manufacturing Engineering}\\
   \large{Department of Mechatronic Engineering}\\
    ------------------------------------------------------------------------------------------------\\[0.1cm]
    \LARGE{\textbf{Design and Fabrication of an Automated Discharge Collection Unit for the Synthetic Hydro-experimental Machine.}}\\[0.1cm]
    \LARGE{\textbf{FYP-18-03}}\\[0.4cm]
    \LARGE{\textbf{INTERIM REPORT}}\\[0.4cm]
    \large{\textbf{Juma Joel Mwimali (ENM221-0060/2017)}}\\[0.2cm]
    \large{\textbf{Kipng'eno Erick  (ENM221-0068/2017)}}\\[0.2cm]
     \large{\textbf{Supervisor}}\\
	\large{Dr. Anthony Muchiri}\\
    \large{\small{\monthyeardate\today}}\\
        ------------------------------------------------------------------------------------------------\\
    \small{Submitted in partial fulfillment of the requirements for the degree of Bachelor of Science in Mechatronic Engineering at Jomo Kenyatta University of Agriculture and Technology, 2022}\\
  \end{center}
\end{titlepage}

\input{Files/Declaration}
\clearpage
\lhead{Abstract}
\input{Files/Abstract}
\clearpage
\tableofcontents
\clearpage
\addcontentsline{toc}{section}{Table of Contents}
\lhead{List of Figures}
\addcontentsline{toc}{section}{List of Figures}
\let\oldnumberline\numberline%
\renewcommand{\numberline}{\figurename~\oldnumberline}%
\listoffigures
\clearpage
\lhead{List of Tables}
\renewcommand{\numberline}{\tablename~\oldnumberline}%
\listoftables
\newpage
\clearpage
\lhead{Nomenclature}
\addcontentsline{toc}{section}{Nomenclature}
\input{Files/ListofAbbreviations}
\clearpage
\newpage
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

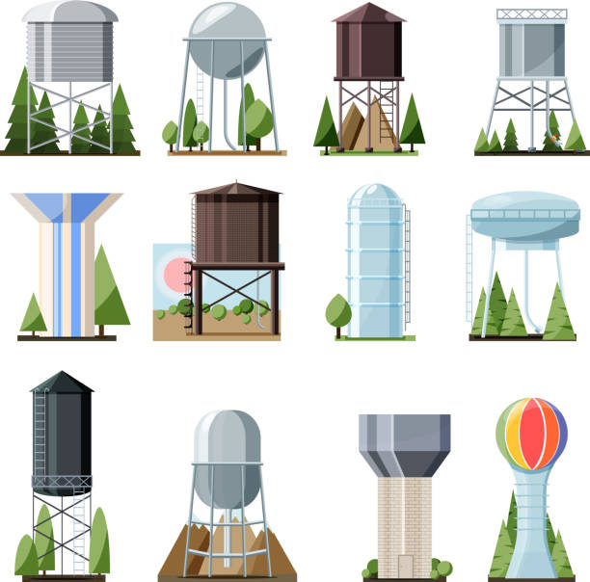
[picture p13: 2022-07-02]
Figures/tankDesigns.jpg

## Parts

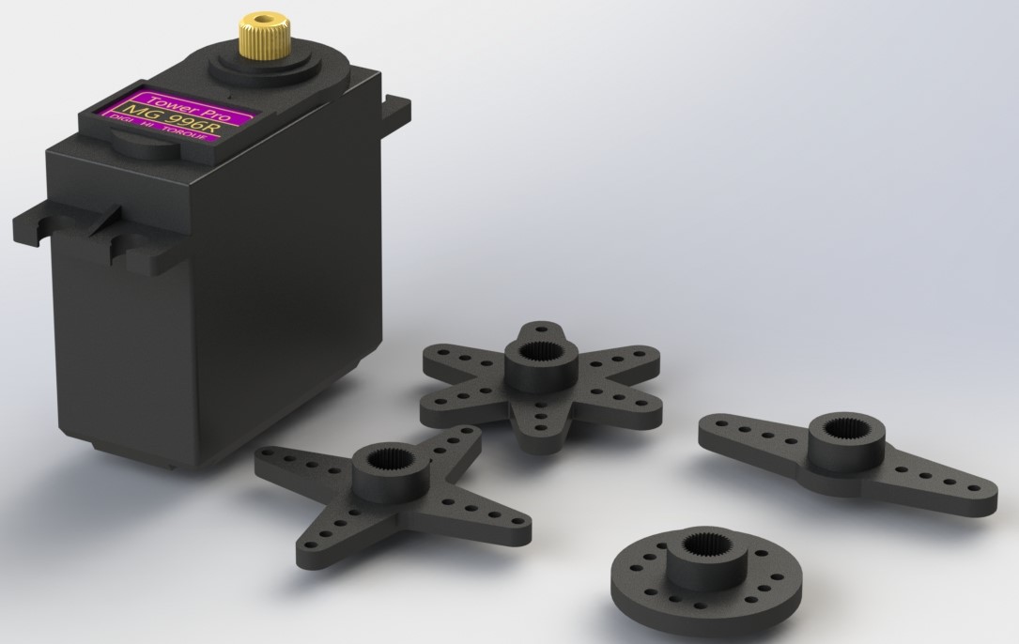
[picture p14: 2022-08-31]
Figures/ServoMotorWithParts.JPG

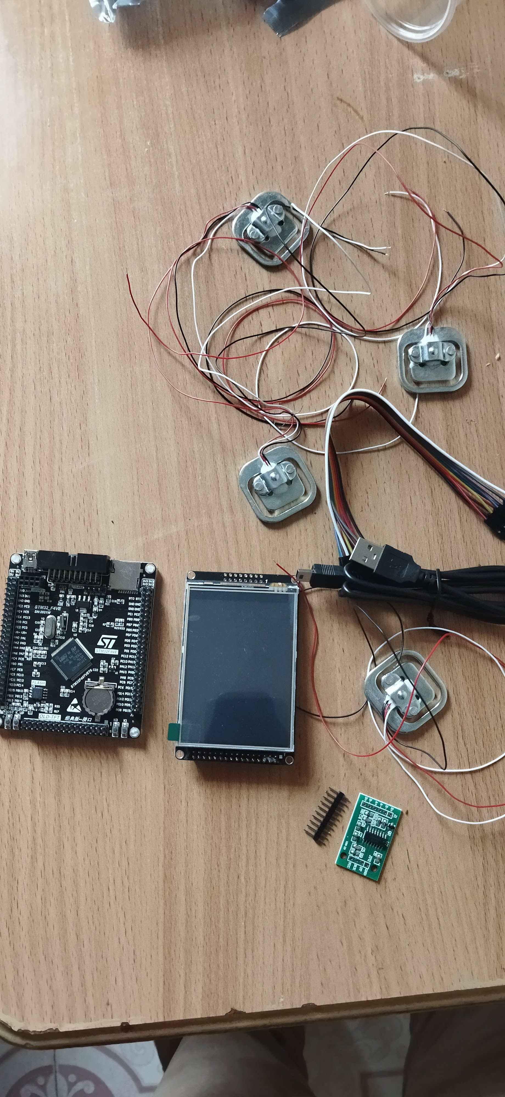
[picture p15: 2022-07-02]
Figures/electronicComponents.jpg

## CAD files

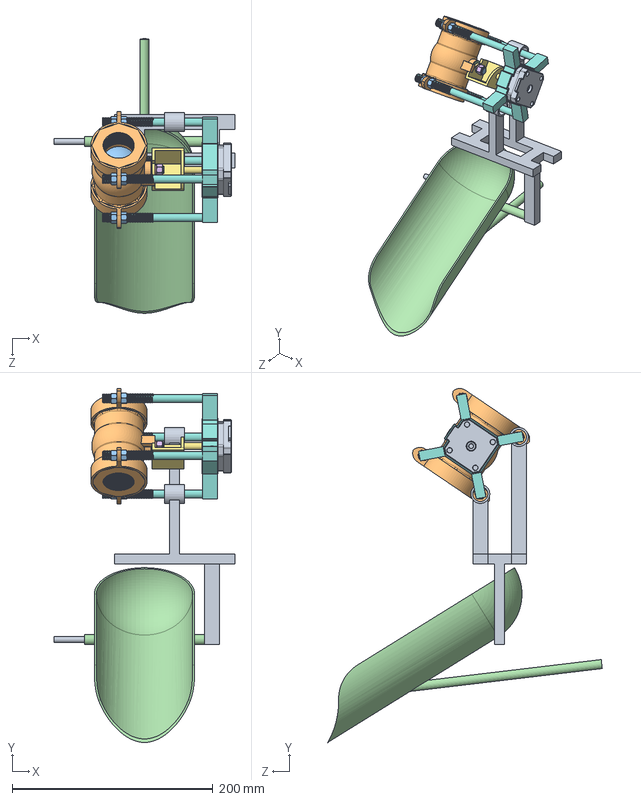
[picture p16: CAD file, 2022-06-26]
designs/DischargeCollection/DiversionUnit.SLDASM
180.0 x 352.8 x 273.7 mm
DiversionSupport
socket
ball
BottomWasher
topWasher
Nut
Interface
MotorCage
Nema17_StepperMotor
strap x 4
Straps Nut x 8
flap

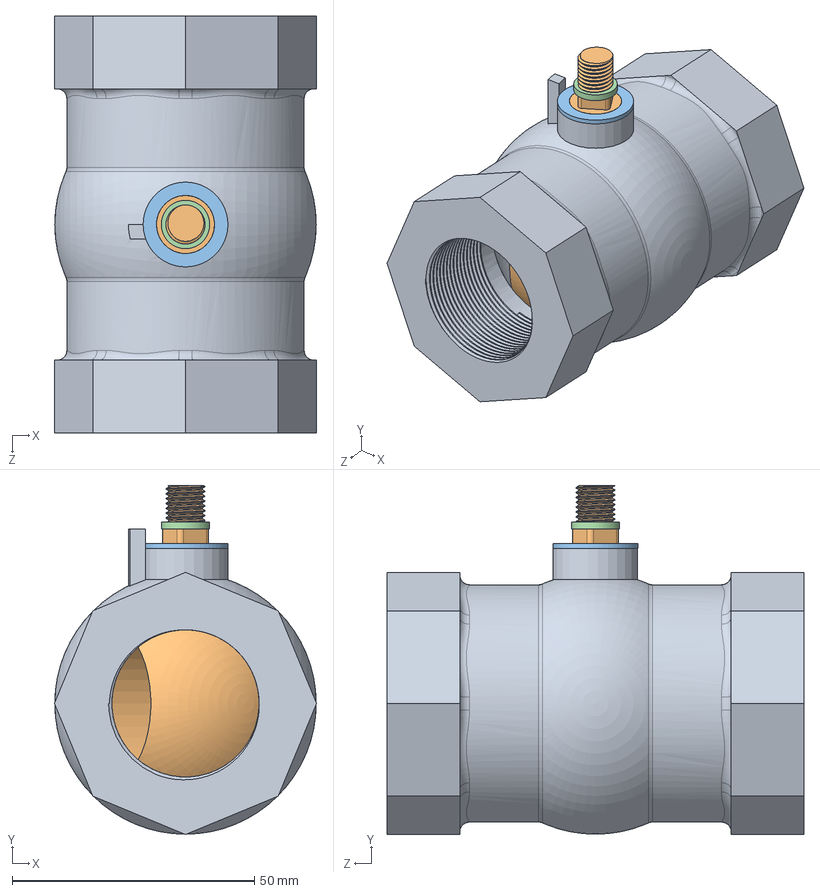
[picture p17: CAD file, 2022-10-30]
designs/DischargeFlowControl/BallValve/BallValve.SLDASM
54.1 x 72.1 x 86.0 mm
socket
ball
BottomWasher
topWasher

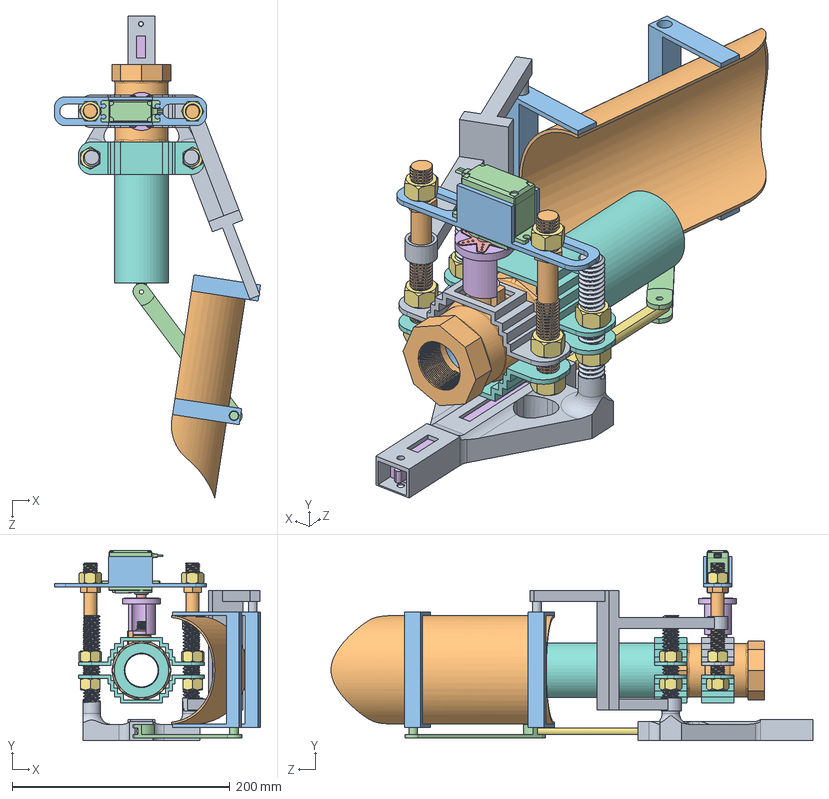
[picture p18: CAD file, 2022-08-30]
designs/DischargeFlowControl/DischargeFlowControlAssembly.SLDASM
189.5 x 175.0 x 443.1 mm
socket
ball
BottomWasher
topWasher
Interface
Nut x 10
twoRailStrapsBottom x 3
twoRailStrapsTop
ServoMotorMountRods x 2
MG996RHolder
MG996RServo
StarSpike
LA-T8Holder
LA-T8Body
LA-T8Rod
SmallPipeExtension
DiversionSupport
flap
FlapHolder x 2
RockerLink

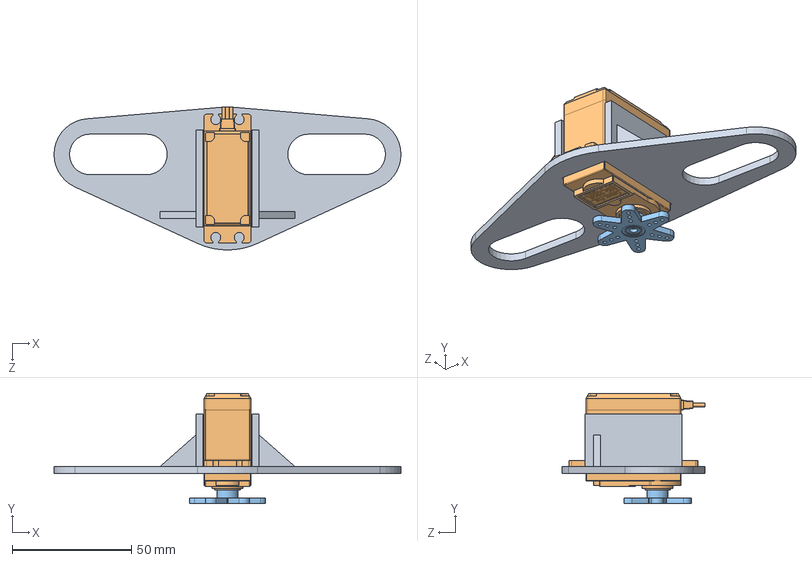
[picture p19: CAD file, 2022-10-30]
designs/DischargeFlowControl/FlowControlSubUnit/MG996RServoMounted.SLDASM
145.6 x 46.4 x 60.0 mm
MG996RHolder
MG996RServo
StarSpike

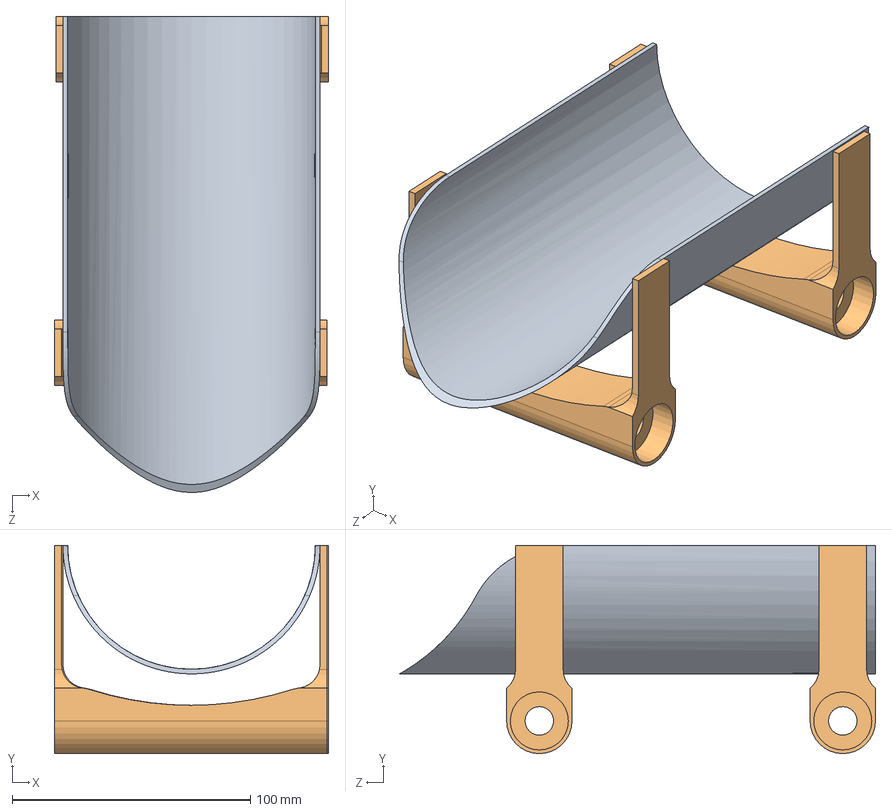
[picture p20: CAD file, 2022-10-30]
designs/DischargeFlowControl/FlowDiversionSubUnit/FlapAssembly.SLDASM
115.2 x 87.5 x 200.0 mm
flap
FlapHolder x 2

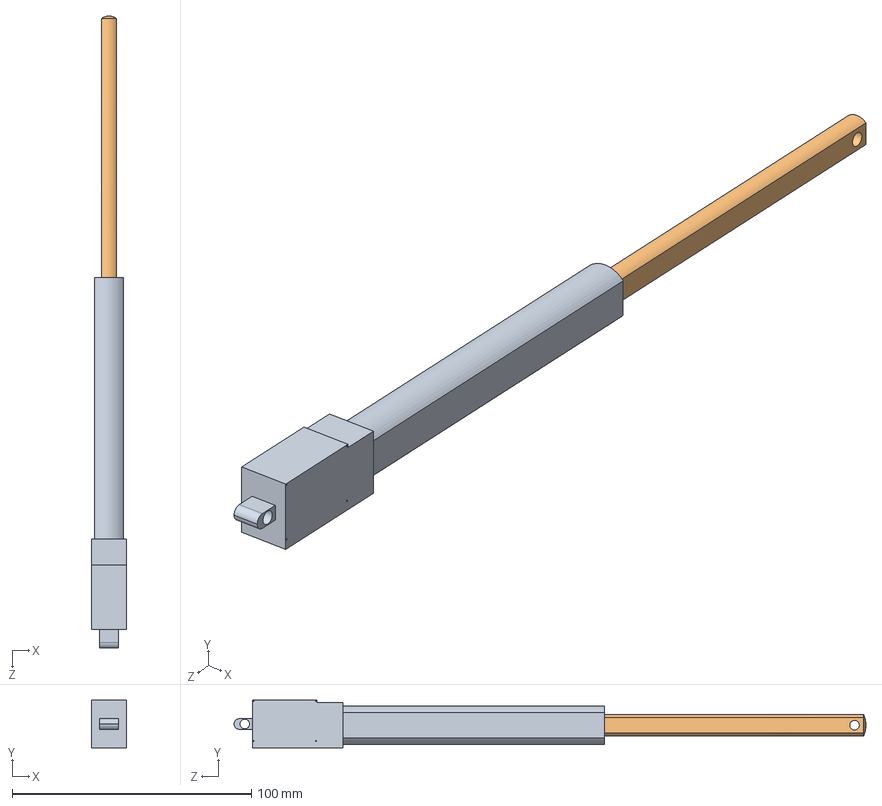
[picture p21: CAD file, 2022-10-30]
designs/DischargeFlowControl/FlowDiversionSubUnit/LA-T8/LA-T8.SLDASM
14.8 x 20.0 x 264.2 mm
LA-T8Body
LA-T8Rod

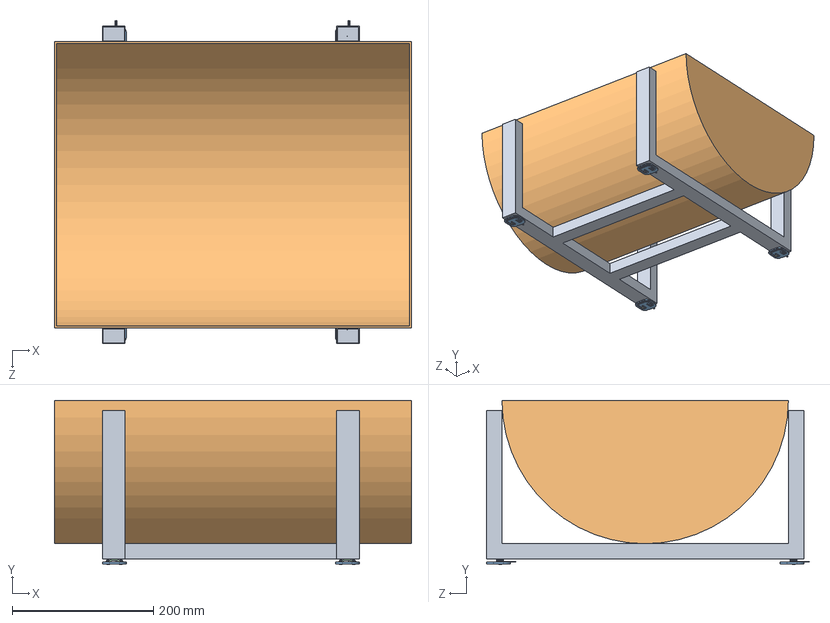
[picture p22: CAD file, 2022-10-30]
designs/DischargeHandlingUnit/CollectionTankWithTheLoadCells.SLDASM
506.0 x 232.5 x 458.0 mm
tankHolder
tank
Base.stp x 4
Top.stp x 4
Cables.stp x 4
Nit.stp x 4
eBom-prt4.stp x 4

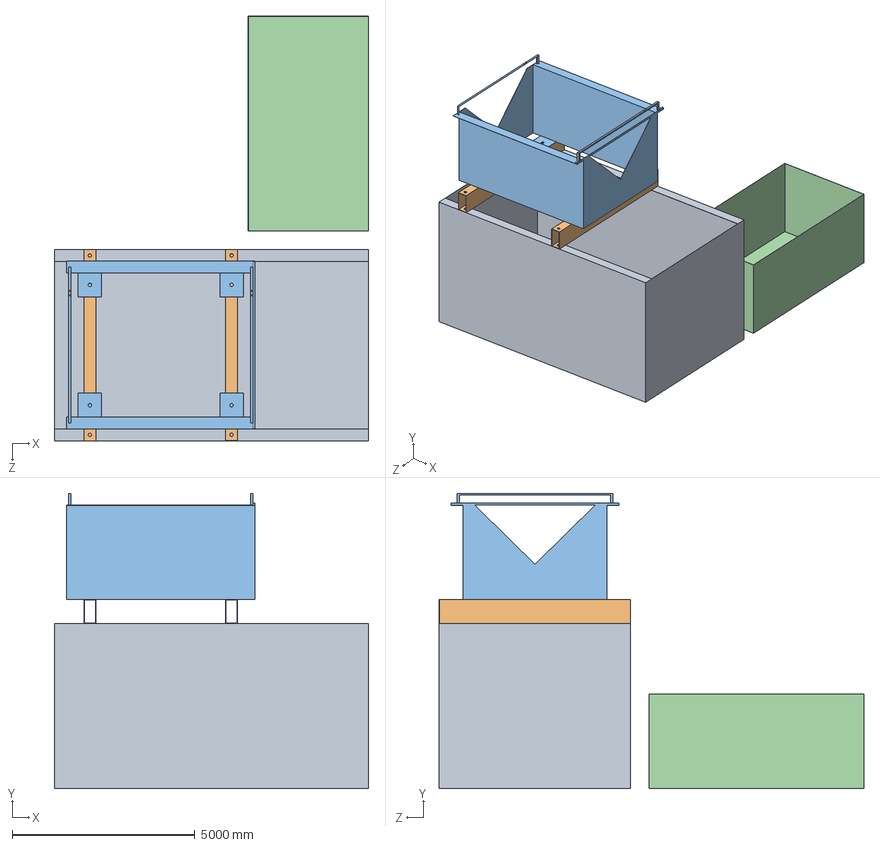
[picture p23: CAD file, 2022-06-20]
designs/SHEM.SLDASM
8580.6 x 8064.5 x 11604.8 mm
MainReservoir
SupportingBar x 2
SupportingReservoir
Minirreservoir

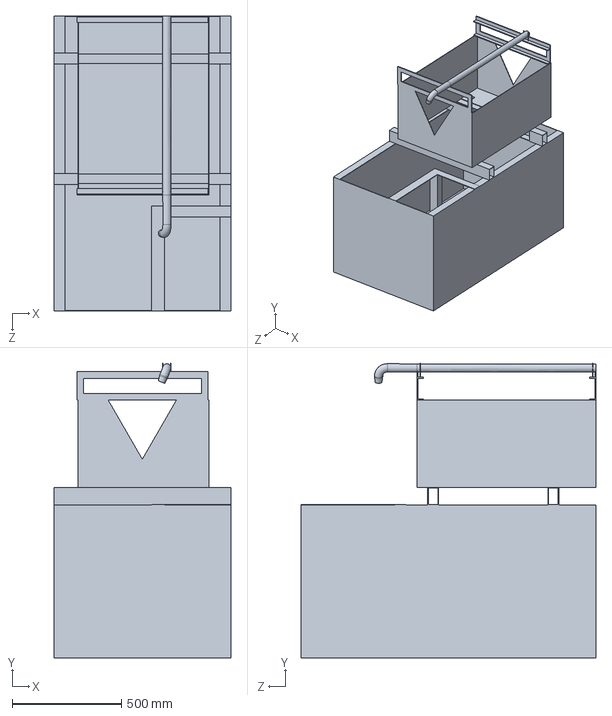
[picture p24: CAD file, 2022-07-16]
designs/SHEM/MainReservoir.SLDPRT
810.0 x 1350.0 x 1350.0 mm

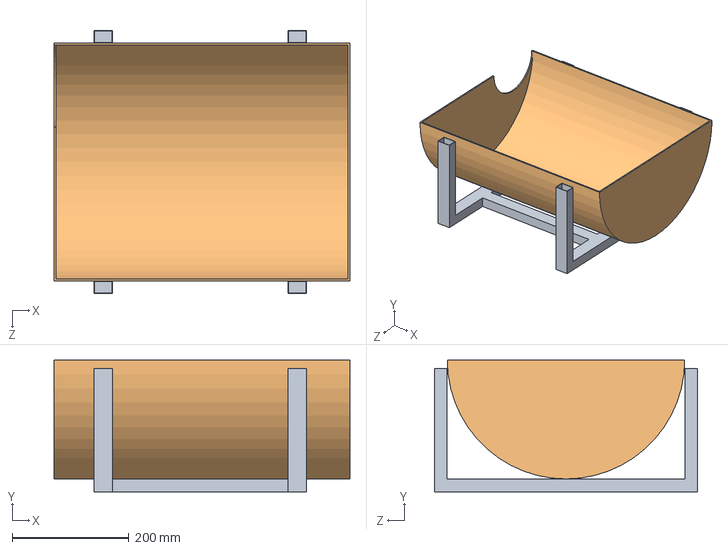
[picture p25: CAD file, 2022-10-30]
designs/DischargeHandlingUnit/Collectiontank/CollectionTank.SLDASM
506.0 x 225.0 x 450.0 mm
tankHolder
tank

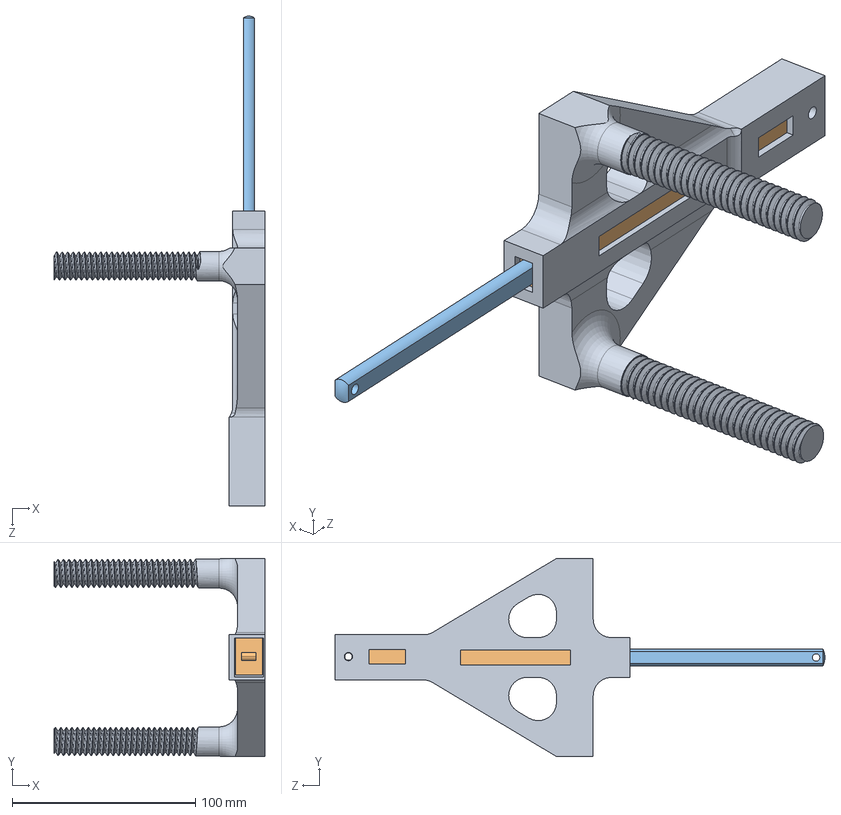
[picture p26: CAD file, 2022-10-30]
designs/DischargeFlowControl/FlowDiversionSubUnit/LA-T8Assembly.SLDASM
115.0 x 108.0 x 267.0 mm
LA-T8Holder
LA-T8Body
LA-T8Rod

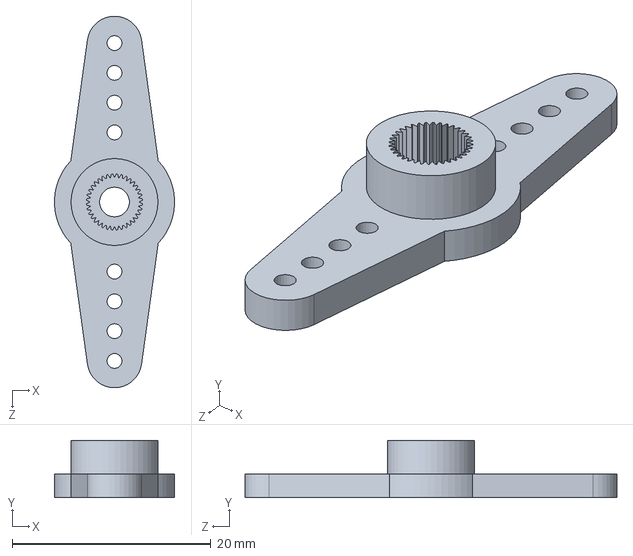
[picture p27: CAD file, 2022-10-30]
designs/DischargeFlowControl/FlowControlSubUnit/MG996R/SingleSpike.SLDPRT
12.1 x 5.75 x 37.4 mm

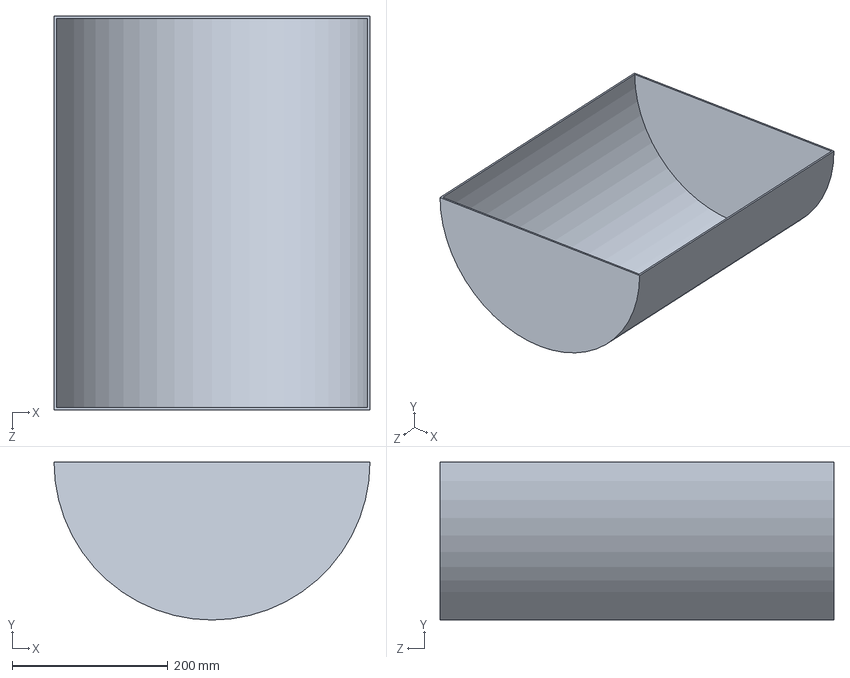
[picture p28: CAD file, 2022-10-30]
designs/DischargeHandlingUnit/Collectiontank/tank.SLDPRT
406.0 x 203.0 x 506.0 mm

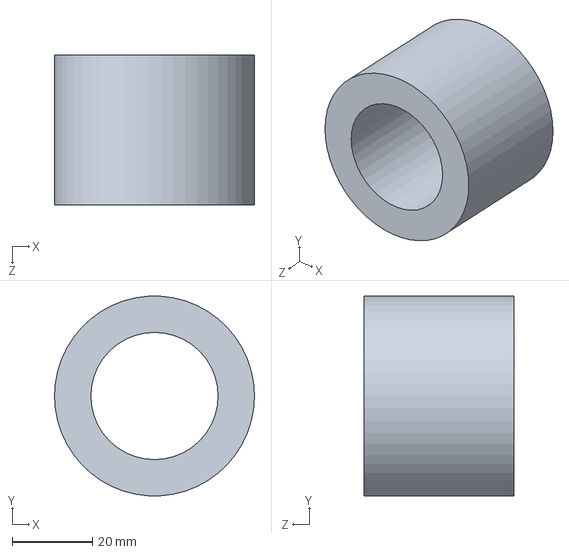
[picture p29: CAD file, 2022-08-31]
designs/DischargeFlowControl/BallValve/SmallPipeExtension.SLDPRT
50.0 x 49.9 x 37.5 mm

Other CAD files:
designs/DischargeFlowControl/FlowControlSubUnit/Interface.SLDPRT
designs/DischargeFlowControl/FlowControlSubUnit/MG996R/WheelySpike.SLDPRT
designs/DischargeFlowControl/FlowDiversionSubUnit/LA-T8/LA-T8Body.SLDPRT
designs/DischargeFlowControl/FlowDiversionSubUnit/LA-T8Holder.SLDPRT
designs/DeprecatedDesigns/BallValveAssembly.SLDASM
designs/DeprecatedDesigns/CrankLink.SLDPRT
designs/DeprecatedDesigns/DischargeContainerVersion1.SLDPRT
designs/DeprecatedDesigns/Electromagnet/Coil.SLDPRT
designs/DeprecatedDesigns/Electromagnet/Electromagnetic Actuator.SLDASM
designs/DeprecatedDesigns/Electromagnet/casing.SLDPRT
designs/DeprecatedDesigns/Electromagnet/rod.SLDPRT
designs/DeprecatedDesigns/Electromagnet/spring.SLDPRT
designs/DeprecatedDesigns/ElectromagnetAssembly.SLDASM
designs/DeprecatedDesigns/ElectromagnetHolder.SLDPRT
designs/DeprecatedDesigns/MG995Servo.SLDPRT
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

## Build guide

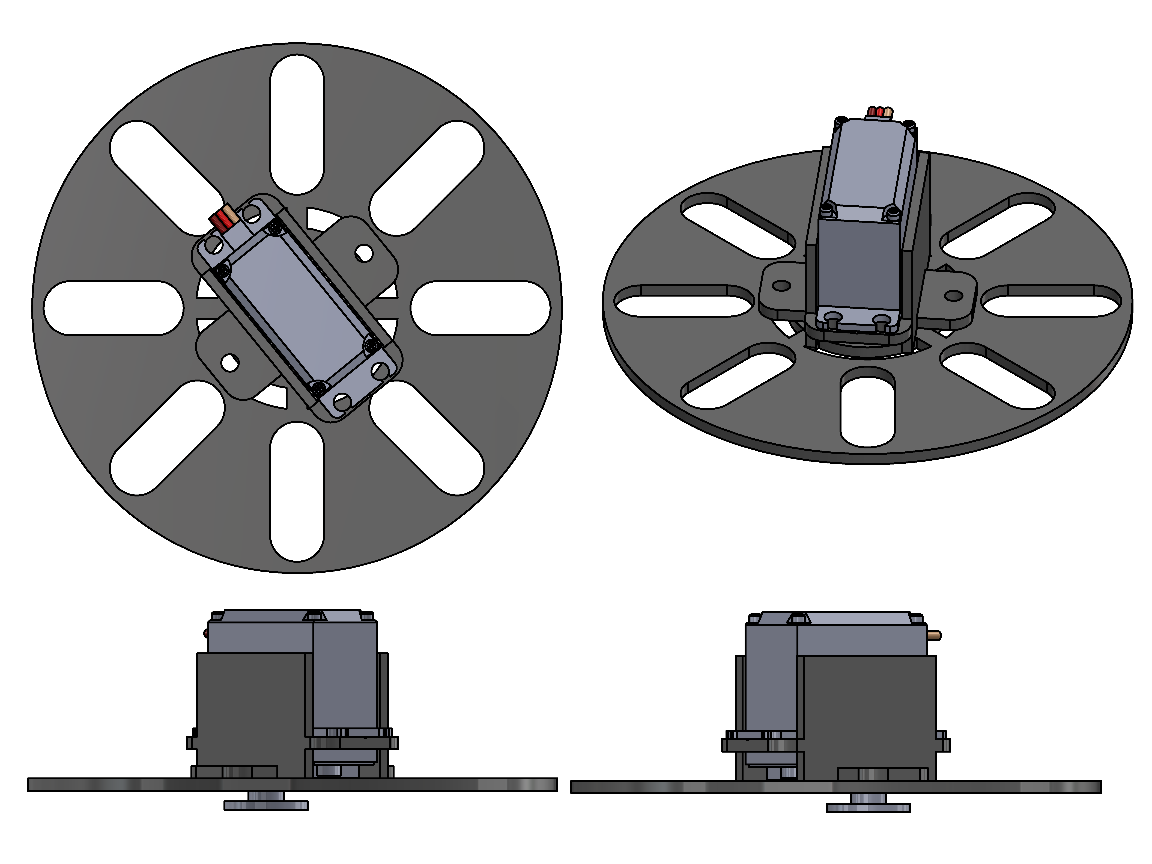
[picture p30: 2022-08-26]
presentations/images/ServoMotorMountedAssembly.PNG

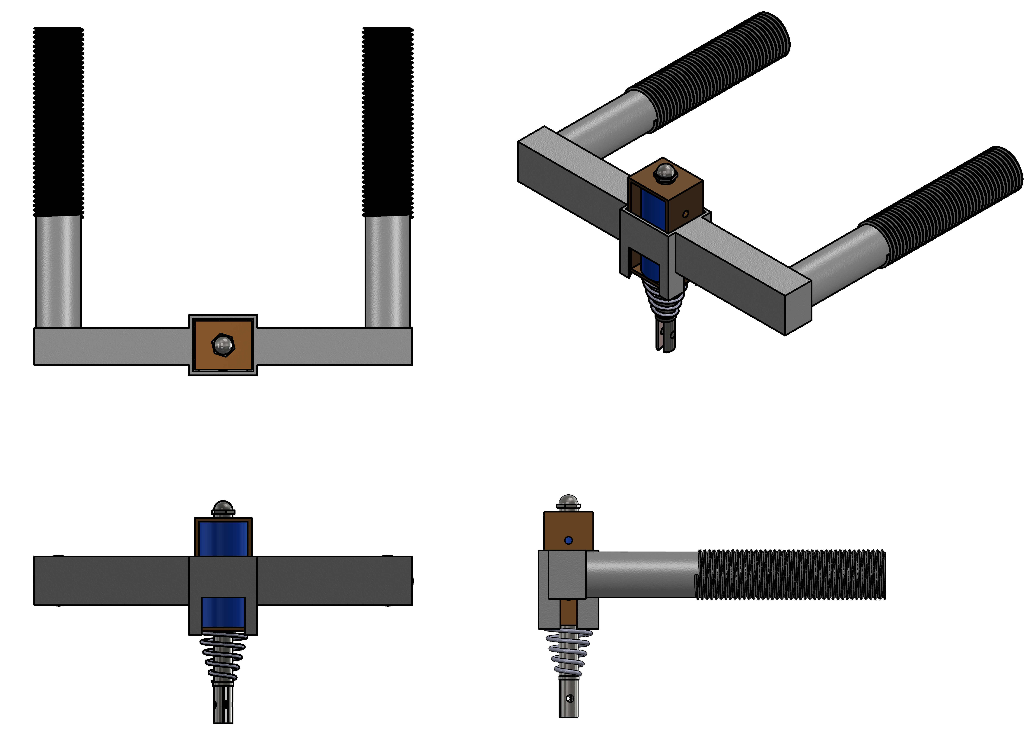
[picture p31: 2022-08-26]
presentations/images/ElectromagnetAssembly.PNG

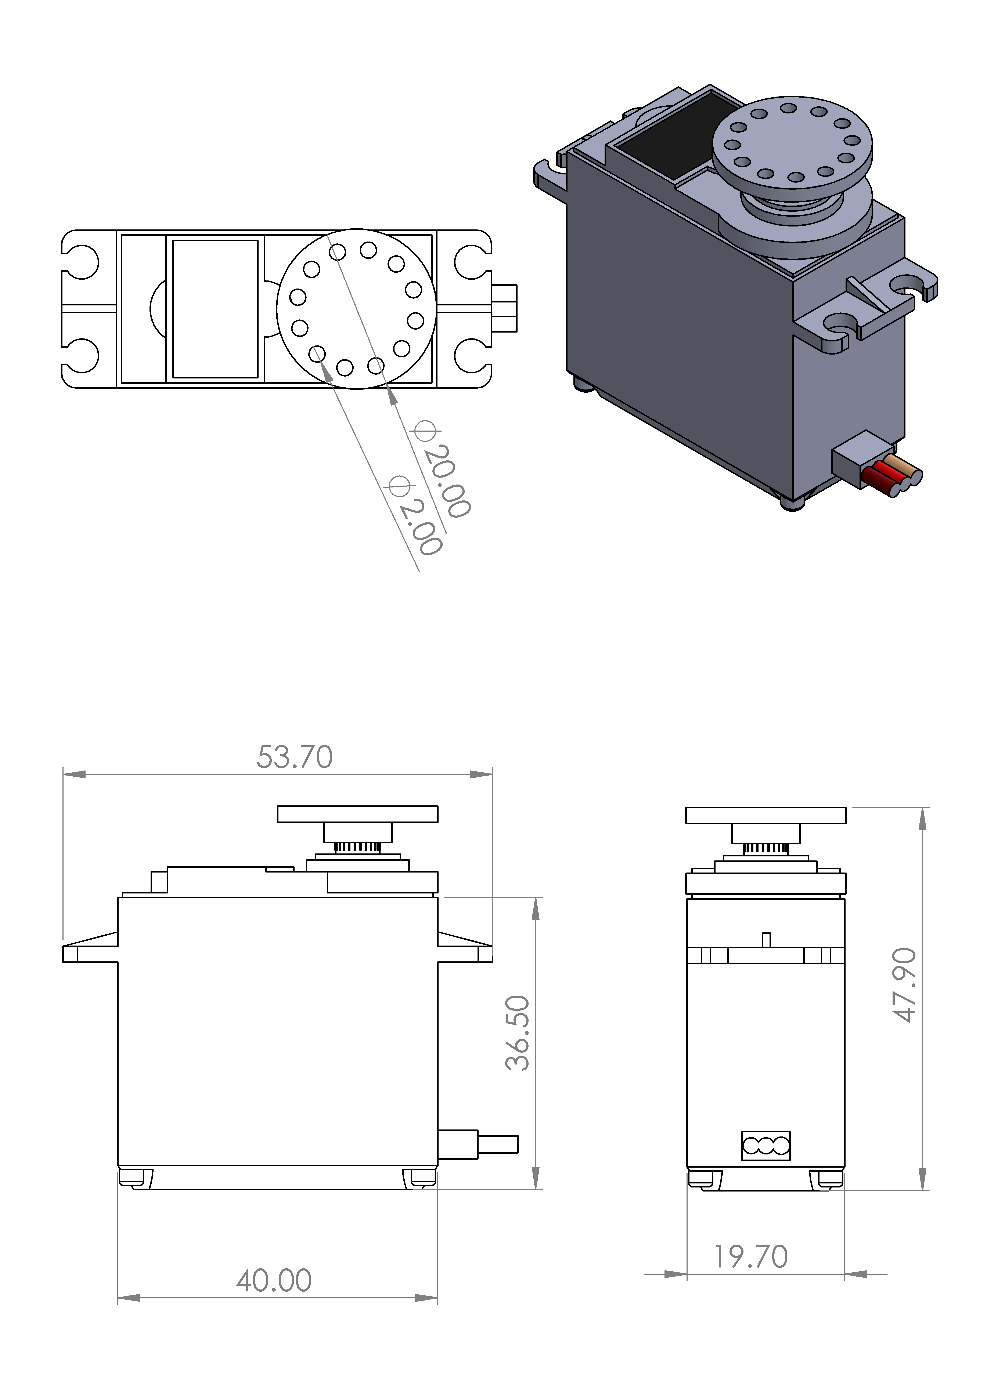
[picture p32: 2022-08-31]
Figures/ServoMotorAssembly.PNG

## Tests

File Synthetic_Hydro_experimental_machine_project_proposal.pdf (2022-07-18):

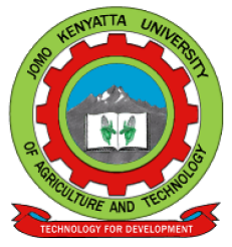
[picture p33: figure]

### Jomo Kenyatta University of Agriculture and Technology

### College of Engineering and Technology

### School of Mechanical, Materials, and Manufacturing Engineering

### Department of Mechatronic Engineering

————————————————————————————————

# FYP-18-03

# Design and Fabrication of an Automated

# Discharge Collection Unit for the Synthetic

Hydro-experimental Machine.

# INTERIM REPORT

### Juma Joel Mwimali (ENM221-0060/2017)

### Kipng’eno Erick (ENM221-0068/2017)

### Supervisor

### Dr. Anthony Muchiri

July, 2022

Submitted in partial fulfillment of the requirements for the degree of Bachelor of Science in

Mechatronic Engineering in Jomo Kenyatta University of Agriculture and Technology, 2022

————————————————————————————————

I

## Declaration

We hereby declare that the work contained in this report is original; researched and

documented by the undersigned students. It has not been used or presented elsewhere

in any form for award of any academic qualification or otherwise. Any material obtained

from other parties have been duly acknowledged. We have ensured that no violation of

copyright or intellectual property rights have been committed.

1. Juma Joel Mwimali
Signature | Date |
2. Kipng’eno Erick
Signature | Date |

Approved by:

Supervisor: Dr. Anthony Muchiri

Signature | Date |

II

## Abstract

The synthetic hydro-experimental machine used for fluid mechanics experiments in the

fluids lab at Jomo Kenyatta University employs an older technology in the measurement

of the dynamic pressure component in fluids. The machine is wholly mechanical as most

of the parameter manipulations and measurements are done mechanically. During fluid

flow experiments such as determining the coefficient of discharge for the Venturi and the

orifice, one controls the flow rate by opening the gate valve in small steps by hand, reads

the differential pressure from the alcohol manometers, measures the temperature, and

time of the discharge simultaneously, and finally the weight of the discharge. The step

size can be inconsistent since it is determined by human intuition. The initiation of time

and temperature measurement is to be synchronized with discharge collection. This is

of course not usually the case with this machine since it is mechanical and cannot be

achieved by a human. These limitations result in a huge error margin in the calculation

of the coefficient of discharge.

This project proposal seeks to reduce this error margin while maintaining the credibility of

the experiment through the automation of the discharge collection unit. This will involve

precisely controlling the gate valve in steps, and automating the discharge collection

mechanism by techniques such as precisely collecting the discharge in steps, digitizing the

temperature, time, and weight measurement of the discharge, and reducing environmental

influence on these measurements. An ergonomic user interface would also be integrated

to allow for parameter manipulations and monitoring.

This automation is expected to reduce the oftenly huge error margins in fluid flow exper-

iments due to human errors.

III

## Contents

Declaration | I
Abstract | II
List of Figures | V
List of Tables | VI
List of Abbreviations | VII
1 Introduction | | 1
1.1 Background | | 1
1.2 Problem statement | | 1
1.3 Objectives | | 2
1.3.1 | Main objective | | 2
1.3.2 | Specific objectives | | 2
1.3.3 | Expected outcomes | | 2
1.4 Justification | | 3
2 Literature Review | | 4
2.1 Introduction | | 4
2.2 Existing Technologies | | 4
2.2.1 | Computational Fluid Dynamics | | 4
2.2.2 | Analytical Predictions | | 6
2.3 Related Works | | 8
2.3.1 | Electromagnetic activation | | 8
2.3.2 | Pneumatic Control | | 9
2.4 Summary | | 9
2.5 Gap analysis | 10

CONTENTS | IV

### 3 Methodology | 12

3.1 Overview | 12
3.2 Discharge flow control unit | 12
3.3 Design Consideration | 12
3.3.1 | Stepper Motor | 12
3.3.2 | Servo Motor | 13
3.4 Justification | 13
3.5 Flow Control Unit Designs | 14
3.6 Discharge collection unit | 14
3.6.1 Flow diversion sub-unit | 14
3.7 Design Consideration | 15
3.7.1 | Piezoelectric Actuators | 15
3.7.2 | Electromagnets | 15
3.8 Justification | 16
3.9 Flow Diversion Sub-Unit Designs | 16
3.9.1 | Discharge collection tank | 17
3.9.2 | Outlet valve | 18
3.9.3 | Weight measurement sub-unit | 18
3.9.4 | Temperature measurement sub-unit | 19
3.10 Interface and Control | 20
3.10.1 Processing sub-unit | 20
3.10.2 Interface | 22

### 4 Results and Discussion | 24

### 5 Conclusion | 25

References | 26

V

## List of Figures

Figure 2.1 Test loop schematic [1] | | 5
Figure 2.2 Experimental setup [2] | | 6
Figure 2.3 Venturi meter | | 7
Figure 2.4 Sampler actuation mechanism [3] | | 9
Figure 2.5 Dispensing mechanism [4] | 10
Figure 3.1 Top View | 14
Figure 3.2 Top View | 15
Figure 3.3 Diversion Unit front View | 16
Figure 3.4 Diversion Unit side View | | 17
Figure 3.5 Diversion Unit isometric View | | 18
Figure 3.6 Application logic | 21

VI

## List of Tables

Table 2.1 Calculated Cd | | | 5
Table 2.2 Results | | 6

LIST OF TABLES | VII

## List of Abbreviations

GPIO General Purpose Input Output

CFD Computational Fluid Dynamics

SKE Single Kernel Estimate

MAWS Automatic Water Sampler

UMV Unmanned Marine Vehicle

Chapter 1. Introduction | 1

## 1 Introduction

### 1.1 Background

Fluid flow measurement involves the measurement of the properties of a smooth and

uninterrupted stream of flowing particles that conform to a pipe. These flow properties

include the coefficient of discharge, mass flow rate, fluid velocity, differential pressure, and

conductivity coefficients. They are altered and measured by flow measuring devices such

as the Venturi, the Orifice, turbine flow meters and rotameters [5]. These measurements

are finally related to the flow using the Bernoulli’s equation.

The Synthetic Hydro-Experimental machine, currently installed in JKUAT, is a config-

urable machine with these flow meters. This machine is used to conduct experiments to

establish relationships between the fluid flow properties and the behavior of the flow. It

has a lift pump, gate valves, alcohol manometers, pressure gauges, a Pelton turbine, a

Venturi, an orifice, and water reservoirs. During experiments, the lift pump is turned on,

and the discharge valve is fully opened to establish a steady flow. The discharge valve

is then closed. The valve is opened in small steps depending on the number of steps re-

quired. For each step, the discharge is collected, and its temperature is measured within

a specific time interval. Finally, the weight of the collected discharge is also measured.

### 1.2 Problem statement

In fluid flow experiments involving the Venturi, and the orifice, the discharge steps are to

be precisely opened, and the time and temperature measurements are taken simultane-

ously with discharge collection in order to obtain values that are within a tolerable range.

This is not the case with the Synthetic Hydro-Experimental machine currently used in

JKUAT since it is wholly mechanical and some of the simultaneous measurements cannot

be simply achieved by a human. The flow rate is controlled by a gate valve in small steps

determined by human intuition which can be inconsistent. With these inconsistencies,

the results can often be outside the tolerable range. Automating the discharge collec-

tion process can minimize the error in the results and still preserve the credibility of the

Chapter 1. Introduction | 2

experiment.

### 1.3 Objectives

### 1.3.1 Main objective

The main objective of this project is to automate the discharge collection process for the

Synthetic Hydro-Experimental machine.

### 1.3.2 Specific objectives

1. To design an automated discharge flow control unit that can precisely discharge in

steps.

2. To design and fabricate a discharge collection unit with automated weight, time and

temperature measurements.

3. To design a user interface and the control algorithm.

### 1.3.3 Expected outcomes

The following are what are expected of the specific objectives mentioned

1. Discharge flow control unit

A discharge flow control control mechanism that can turn the ball valve in precise

steps is expected. The steps obtained from the division of the circumference of a

full turn by the number of steps are also expected to be precise to the nearest whole

number.

2. Discharge collection unit

A discharge collection unit that can precisely collect the discharge within the speci-

fied time interval while taking its temperature and weight is expected. This can be

expected if the expectations of the following sub-units are met :

(a) Flow diversion sub-unit

A precisely sized diversion sub-unit, correctly positioned to collect the whole

Chapter 1. Introduction | 3

stream is expected. This will improve on the accuracy of the weight of the

discharge and hence that of the experiment.

(b) Discharge collection tank

A discharge collection tank whose shape can allow for accurate weight mea-

surement is expected. It is also expected that this tank is positioned in such a

way that flow into this tank utilizes gravity to eliminate the need for an extra

pump.

(c) Discharge weight and temperature measurements

It is expected these units measuring devices can measure to the smallest reso-

lution.

3. Control and Display

It is expected that the control module can handle intense computations such as error

approximation, immediate rendering of results and communicating with the sensors

and transducers that will be used in the system. It is also expected that the user

interface is slick and ergonomic.

### 1.4 Justification

This automation will simplify the discharge collection process and ensure consistency and

precision of the results obtained in each step during fluid flow experiments done on the

machine. With such automation, one person can also singly complete the experiment

with not much strain as opposed to the current state. The automated system will also be

modular that it can be easily mounted and dismounted from the main machine with no

major adjustments.

Chapter 2. Literature Review | 4

## 2 Literature Review

### 2.1 Introduction

Fluid flow experiments involve collecting the discharge within specific time intervals. This

is usually done simultaneously with the temperature measurement of the discharge in

order to minimize the environmental effect on this reading. The weight of the discharge

is finally measured for the computation of the mass flow rate property of the flow.

### 2.2 Existing Technologies

Some advanced and even rudimentary technologies have been used in place of the Syn-

thetic Hydro-Experimental machine for the determination of fluid flow properties. The

technologies include :

### 2.2.1 Computational Fluid Dynamics

Computational Fluid Dynamics (CFD) is a powerful modelling and analysis technique

that utilizes finite difference techniques to solve highly non-linear differential equation of

pressure, energy, relative humidity, air temperature and velocity [6]. It can be used to

model fluid flow in flow measurement devices.

Tukimin et al [1] conducted a CFD analysis using an Single Kernel Estimate (SKE)

turbulence model to determine the coefficient of discharge of a Venturi tube, and finally

compared the results to those obtained from a physical experimental setup. The test loop

shown in figure 2.1 was used both in a physical setup and a CFD model.

They designed a CFD model using the ANSYS Design Modeller software. The model

consists of a Venturi tube, designed according to the standards ISO 5167:2003 [7], and a

liquid and gas system. They did a physical experiment using the same test matrix used

in the numerical simulation model. Finally, they computed the coefficient of discharge of

the venturi using equationt 2.1.

Chapter 2. Literature Review | 5

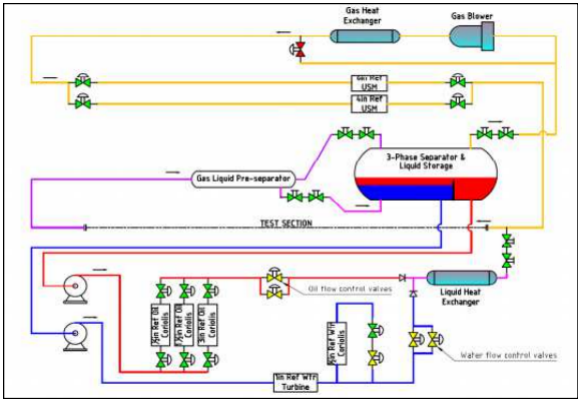
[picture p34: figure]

Figure 2.1: Test loop schematic [1]

Table 2.1: Calculated Cd

Venturi under Test Average Discharge Coefficient Average Discharge Coefficient
From experiment | From CFD post
Venturi 1 0.99366 | 0.984347

Cd =

4m

p
1 − β

4
πεd²

√
200000Dp1ρ1

(2.1)

The results obtained in 2.1 showed a difference of less than 1% between the Cd obtained

from the two setups.

Tamhankar et al [2] also did a similar experiment using a CFD model designed in ANSYS

Fluent 13.0 utilizing a Realizable k-ϵ turbulence model which is superior to a Standard

k-ϵ turbulence model and compared the results to those obtained from an experimental

setup show in figure 2.2.

Chapter 2. Literature Review | 6

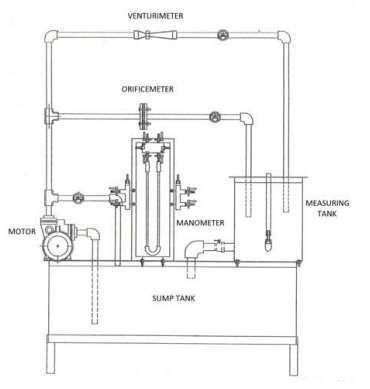
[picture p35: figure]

Figure 2.2: Experimental setup [2]

Table 2.2: Results

Reading No. | Experiment | CFD analysis
1 | 0.9724 | 0.9619
2 | 0.9592 | 0.9689
3 | 0.9779 | 0.9692

Table 2.2 shows the results obtained from the study

The study concluded that difference in values of the coefficient of discharge obtained from

the model and those obtained from the experimental setup was less than 5% .

### 2.2.2 Analytical Predictions

This technique utilizes the Bernoulli’s equation to establish an analytical correlation be-

tween the fluid flow and the coefficient of discharge of the Venturi meter.

Figure 2.3 shows the Venturi meter. Assuming the flow is ideal and applying the Bernoulli’s

Chapter 2. Literature Review | 7

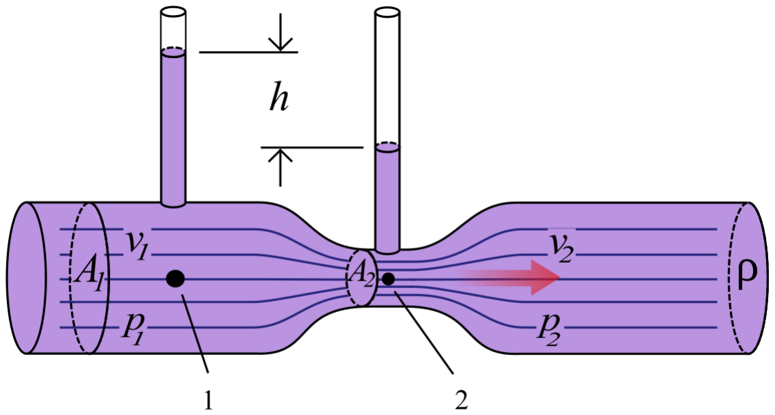
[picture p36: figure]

Figure 2.3: Venturi meter

equation before and after the contraction,

p1
ρg

+

v

2
1
2g

+ z1 =

p2
ρg

+

v

2
2
2g

+ z2

But Z1 = Z2,
(p1 − p2)
ρ

=

(v

2
2 − v

2/1)
2
(p1 − p2)
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
1 − β

4

v2 =

1
p
1 − β

4

s
2∆p
ρ

(2.2)

Applying the continuity equation to the result of the derivation in 2.2,

Qth = A1v1 = A2v2

Qth = A2v2 =

1
p
1 − β

4

πd²
4

s
2∆p
ρ

(2.3)

Equation 2.3 of theoretical flow rate is based on the assumption that the flow is steady,

incompressible, inviscid, irrotational, no losses and the velocities V1 and V2 are constant

across the cross section [8].

Chapter 2. Literature Review | 8

Qact = p

Cdstd
1 − β

4

πd

2
4

s
2∆p
ρ

(2.4)

The frictional and viscous losses in a laminar flow can be estimated by the Darcy’s law

HL =

(∆p)viscous
ρg

= f v

2
2 g

D
D

(2.5)

where ’f’ is the friction factor.

Coefficient of discharge equation 2.7 where for laminar flow, ’f’ is given by equation 2.6 .

This equation is derived from both the Darcy’s law equation and the theoretical flow rate

equation 2.3.

f =

64

Red

(2.6)

Cd = 0.995s
1
(1 + 3f)

(2.7)

Arun et al [8] did a comparision of the Cd obtained by this method and that obtained

from a CFD simulation. The study concluded that the results from the two methods had

an uncertainty of 0.9%.

### 2.3 Related Works

Discharge collection techniques have been developed for various applications. Some of

these applications are related to the discharge collection unit used in the Synthetic Hydro-

Experimental machine.

### 2.3.1 Electromagnetic activation

Angelo et al [3] implemented this technique in the design and testing of an Modu-

lar Automatic Water Sampler (MAWS). They designed MAWS and mount them on

Unmanned Marine Vehicle (UMV) with the aim of collecting water samples for scientific

Chapter 2. Literature Review | 9

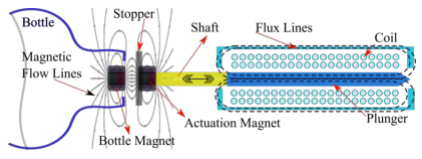
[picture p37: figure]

Figure 2.4: Sampler actuation mechanism [3]

campaigns in front of polar tidewater glaciers. Their main design considerations was the

response time of the stopper since the MAWS were operated under water and at the risk

of damage by glaciers. The actuation unit of the sampler is shown in figure 2.4.

When the coil in the solenoid is crossed by a current a strong magnetic field is gener-

ated that attracts the ferromagnetic plunger connected to the sealing stopper and opens

the bottle allowing water to flow into the bottle’s neck. As the current stops the two

permanent magnets attract each other and the stopper seals the bottle [3].

### 2.3.2 Pneumatic Control

Pneumatic actuators utilizes the power of compressed air to impart motion on objects.

Sangmin, and Joonwon [4] did a design of cartridge-type pneumatic dispenser with a back

flow stopper. The system used a membrane covering a discharge hole. The membrane was

opened and closed using negative and positive pneumatic pressure respectively as shown

in figure 2.5.

The application was able to do precise dispensation of 100nL to 400nL droplets.

### 2.4 Summary

Every fluid flow experiment done on the Synthetic Hydro-Experimental machine involves

the collection of discharge and the measurement of its properties. The most common

experiment is the determination of the coefficient of discharge of the Venturi and the

Orifice. In this literature, other techniques such as CFD and analytical methods have

Chapter 2. Literature Review | 10


Figure 2.5: Dispensing mechanism [4]

been found to be effective as alternatives to this machine. These techniques have been

proven to produce results with a difference of less than 1% from the experimental results

obtained from a physical setup. Such results can also be obtained from the fluids rig

currently used in JKUAT by automating the discharge collection unit. With regard to

this, the literature has also covered discharge collection techniques that have proven to be

effective in other applications and can be adapted for this automation. This techniques

include the application of pneumatics and electromagnetism.

### 2.5 Gap analysis

1. The use of the CFD method or the analytical method undermines the credibility of

the fluid flow experiments. This two techniques are rather used for the design of

fluid flow measuring devices.

2. CFD method can also be very resource intensive in terms of compute resources.

Softwares used for this method requires a hefty license fee.

3. The application of the analytical method involves tedious calculations and several

assumptions which can produce untrustworthy results.

Chapter 2. Literature Review | 11
4. The use of the Synthetic Hydro-Experimental machine with a manual discharge

collection unit often produce results with huge error margins.

This project proposal will be entirely focused on addressing gap number four with the

application of techniques such as pneumatics or electromagnetism. This will close in the

technological gap with the use of CFD, and simplify the use of analytical methods by

providing data for the computation of fluid flow properties.

Chapter 3. Methodology | 12

## 3 Methodology

### 3.1 Overview

This project consists of three main units: a discharge flow control unit, a discharge

collection unit, and a main control unit.

### 3.2 Discharge flow control unit

The unit is used for controlling the flow rate at the end of the pipe system ideally by

allowing a regulated amount of water into the collection tank. To ensure little modification

to the current state-of-the-art machine, the flow control unit utilizes the existing ball

valve to achieve this operation. Furthermore, to attain the regulated flow, the valve

aperture opens and closes in small and precise steps as specified by the user. Therefore,

to achieve this, the servo motor, hosted on a motor cage and clamped to the valve, is

coupled to the ball valve with help of an interface and controlled by a driver based on the

STM32F40VET6 microcontroller.

### 3.3 Design Consideration

Precision in the opening and closing of the ball valve is key to ensuring that only the

required amount of water is collected within the stipulated time. Servo and stepper

motors were considered to achieve this operation.

### 3.3.1 Stepper Motor

The motor operates by accurately synchronizing position with the pulse signal output

from the controller to the driver, achieving highly accurate positioning and speed control.

Stepper motors feature high torque and low vibration at low speeds ideally below 1500rpm,

ideal for applications requiring quick positioning in a short distance. Furthermore, stepper

motor rotates with a fixed step angle typically 1.8 degrees for a 2-phase. However, to

achieve this requires the use of a micro-step driver.

Besides, while having full control of rotation and speed, the simple structure of stepper

Chapter 3. Methodology | 13

motors is achieved without using electrical components, such as an encoder within the

motor. For this reason, stepper motors are very robust and have high reliability with very

few failures. As for stopping accuracy, ±0.05° (without cumulative pitch errors) is very

accurate. Because the positioning of stepper motors is performed by open-loop control and

operated by the magnetized stator and magnetic rotor with small teeth, stepper motors

have a higher follow-up mechanism toward commands than that servo motors. Also, no

hunting occurs when stopping stepper motors.

### 3.3.2 Servo Motor

Servo motors run significantly faster than stepper motors, with speeds greater than

1500rpm. This enables servo motors to be used with gearboxes to deliver much higher

torque at useful speeds. They also deliver more consistent torque across the speed range

of the motor. Unlike stepper motors, they do not have holding torque per se. Closed-loop

operation enables the controller/drive to command that the load remain at a specific po-

sition, however, and the motor will make continual adjustments to hold it there. Thus,

servo motors can deliver de facto holding torque. The Servo motor rotates with a fixed

step angle as low as 1 degree with or without the use of a driver. Furthermore, when pow-

ered, servo motors tend to move their shaft position to the zero position, a phenomenon

referred to as hunting.

### 3.4 Justification

Servo motor is used in the discharge flow control unit because of the small step angle

(1 degree) that it can turn as compared to a stepper with a typical step angle of 1.8

degrees. The smaller the angle, the more the number of steps hence the experiment could

be conducted as many times as possible for higher accuracy. Furthermore, the fact that

servo motors do not necessarily need a micro-step driver for their operation reduces the

overall cost.

Chapter 3. Methodology | 14

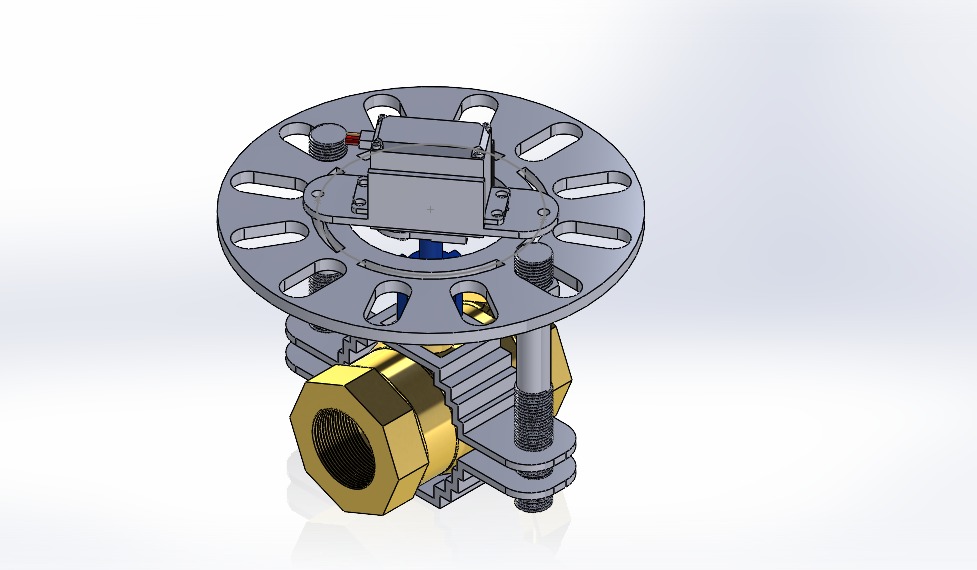
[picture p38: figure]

Figure 3.1: Top View

### 3.5 Flow Control Unit Designs

### 3.6 Discharge collection unit

It is the core part of the experiment. The discharge collection unit comprises the flow di-

version sub-unit, a discharge collection tank, an outlet valve, and weight and temperature

measurements sub-units.

### 3.6.1 Flow diversion sub-unit

The sub-unit is responsible for diverting the discharge from the main pipe system to either

the collection tank or into the main reservoir. The weight of the collected discharge is

critical to the whole process. Therefore, to ensure that only the required amount of water

is collected, the diversion unit ensures that there are minimal splashes and leakages by

use of a curved flap. Furthermore, the fast response of the unit is attained by the use

of an electromagnet whose linear motion is amplified by the use of a lever system hence

providing the flap with a wider angle.

Chapter 3. Methodology | 15

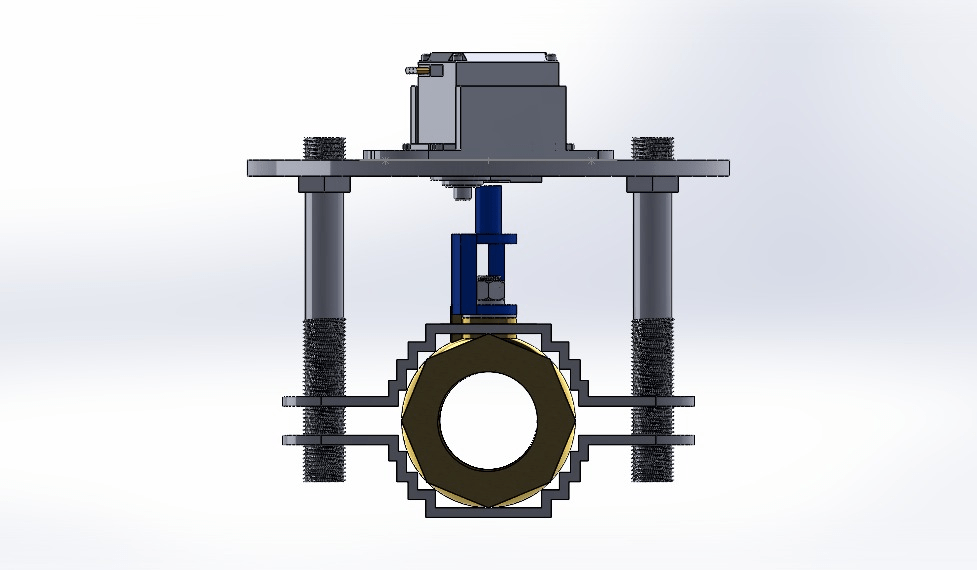
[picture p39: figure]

Figure 3.2: Top View

### 3.7 Design Consideration

The sub-unit is to have a faster response and large linear displacement capabilities Piezo-

electric actuators and electromagnets were considered for this application.

### 3.7.1 Piezoelectric Actuators

Piezoelectric actuators are transducers that convert electrical energy into a mechanical

displacement or stress based on a piezoelectric effect, or vice versa. They are used widely

as a high precision positioning mechanism since they can control a small mechanical

displacement at high speed, with the advantages of large generated force, stable displace-

ment, and ease of use. However, problems include insufficient displacement and the large

voltage up to a few hundred volts, which is needed.
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

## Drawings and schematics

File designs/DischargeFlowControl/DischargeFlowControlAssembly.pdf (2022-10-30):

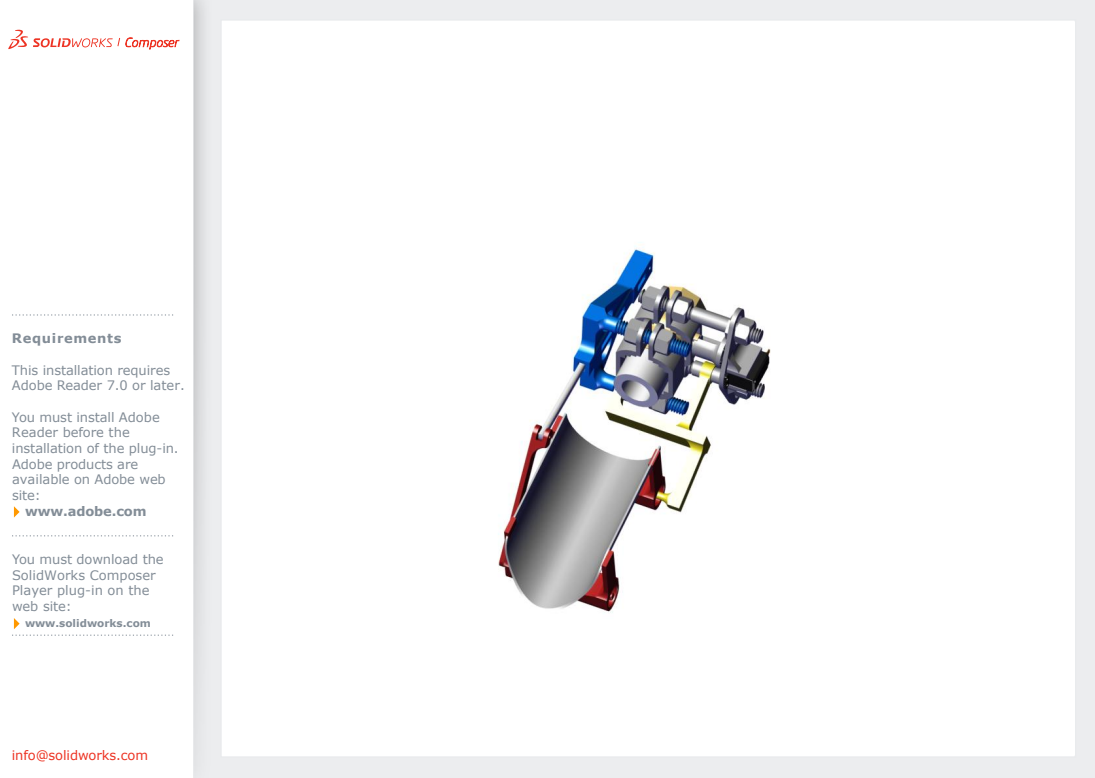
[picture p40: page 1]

Requirements
This installation requires
Adobe Reader 7.0 or later.
You must install Adobe
Reader before the
installation of the plug-in.
Adobe products are
available on Adobe web
site:
www.adobe.com

You must download the
SolidWorks Composer
Player plug-in on the
web site:
www.solidworks.com

info@solidworks.com

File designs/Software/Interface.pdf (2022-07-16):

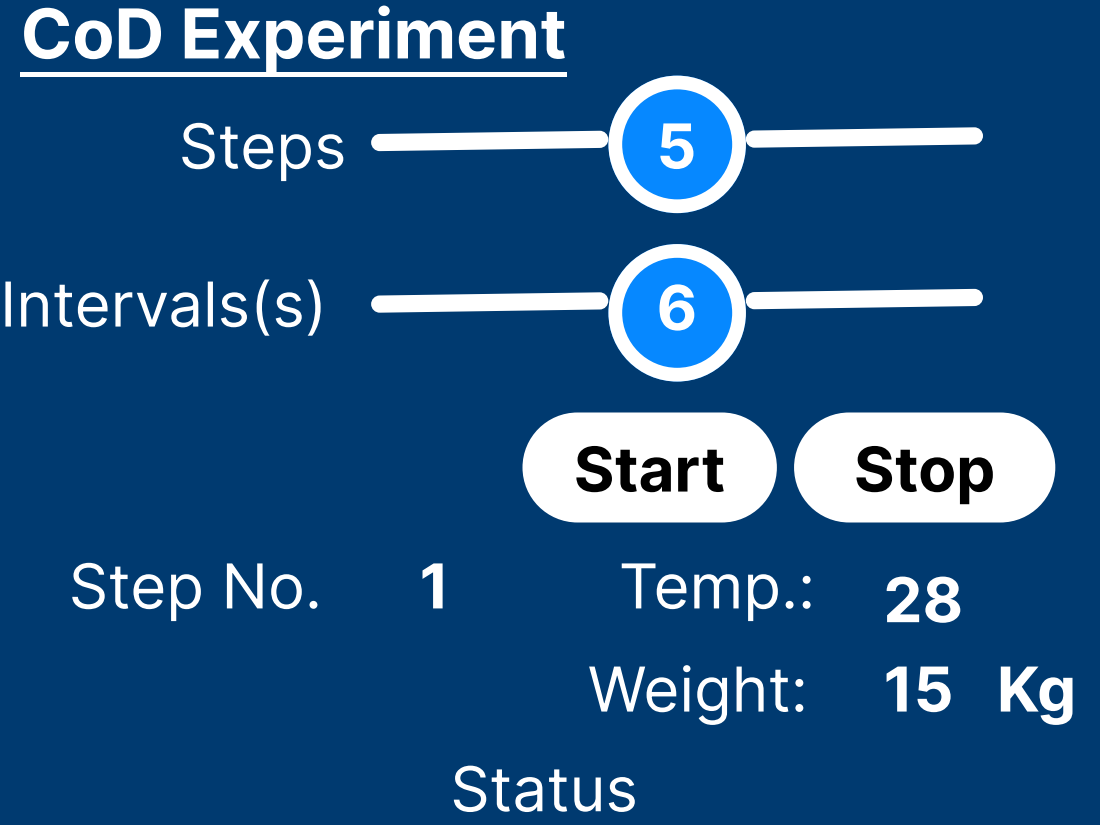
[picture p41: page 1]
CoD Experiment; Steps; Intervals(s); Step No.; Temp.:; Weight:; Status; Start; Stop

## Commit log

2022-06-20 added SHEM replica
    [BallValve.SLDASM, MainPipe.SLDPRT, MainReservoir.SLDPRT, Minirreservoir.SLDPRT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]
2022-06-20 scaled designs from inches to cm
    [BallValve.SLDASM, MainPipe.SLDPRT, MainReservoir.SLDPRT, Minirreservoir.SLDPRT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]
2022-06-20 completed the replication of SHEM
    [BallValve.SLDASM, MainPipe.SLDPRT, PipeBallValve.SLDASM, PipeWithBallValve.SLDASM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]
2022-06-21 added a flap
    [flap.SLDPRT]
2022-06-21 added a discharge collection pipe
    [DischargeCollectingPipe.SLDPRT]
2022-06-22 added an actuation to the flap
    [BallValve.SLDASM, DischargeCollectingPipe.SLDPRT, DischargeContainer.SLDPRT, flap.SLDPRT]
2022-06-22 redesigned the ball valve
    [BallValve.SLDASM, DischargeCollectingPipe.SLDPRT, PipeBallValve.SLDASM, ball.SLDPRT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]
2022-06-22 added the presentation
    [ActuatedBallValve.SLDASM, BallValve.SLDASM, Interface.SLDPRT, Nema17_pancake.step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]
2022-06-26 added the mechanical design of the flow diversion sub-unit
    [ActuatedBallValve.SLDASM, BallValve.SLDASM, BottomWasher.SLDPRT, DischargeContainer.SLDPRT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]
2022-06-27 discharge flow control fully assembled
    [ActuatedBallValve.SLDASM, Coil.SLDPRT, DiversionSupport.SLDPRT, ElectromagnetAssembly.SLDASM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]
2022-06-28 corrected design measurements
    [ActuatedBallValve.SLDASM, DiversionSupport.SLDPRT, ElectromagnetAssembly.SLDASM, Electromagnetic Actuator.SLDASM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]
2022-06-28 added a mechanical design of the collection tank
    [CollectionTank.SLDASM, tank.SLDPRT, tankHolder.SLDPRT]
2022-06-29 redesigned the collection tank support
    [CollectionTank.SLDASM, tank.SLDPRT, tankHolder.SLDPRT]
2022-06-29 made the final assembly of the SHEM machine
    [ActuatedBallValve.SLDASM, CollectionTank.SLDASM, ElectromagnetAssembly.SLDASM, Electromagnetic Actuator.SLDASM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]
2022-06-29 completed the mechanical designs
    [ActuatedBallValve.SLDASM, Coil.SLDPRT, DiversionSupport.SLDPRT, ElectromagnetAssembly.SLDASM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]
2022-06-29 generated a step file for the final assembly
    [ElectromagnetAssembly.SLDASM, Electromagnetic Actuator.SLDASM]
2022-07-02 updated presentations v4
    [ActuatedBallValve.SLDASM, Nema17StepperMotor.SLDASM]
2022-07-02 added a motion study video
    [ActuatedBallValve.SLDASM, ElectromagnetAssembly.SLDASM, Electromagnetic Actuator.SLDASM, Nema17StepperMotor.SLDASM]
2022-07-14 updated designs for ther servo holder
    [BallValveAssembly.SLDASM, CollectionTank.SLDASM, Interface.SLDPRT, MG995Servo.SLDPRT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]
2022-07-16 redesigned parts and redefined dimensions to support the servo approach
    [ActuatedBallValve.SLDASM, BallValve.SLDASM, BallValveAssembly.SLDASM, CollectionTank.SLDASM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]
2022-07-16 mechanical designs completed with part drawings in pdf
    [BallValveAssembly.SLDASM, BallValveAssembly.step, DischargeContainerVersion1.SLDPRT, DiversionSupport.SLDDRW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]
2022-07-22 exploded view generated
    [BallValveAssembly.SLDASM, CollectionTank.SLDASM, DiversionSupport.SLDPRT, ElectromagnetAssembly.SLDASM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]
2022-08-12 orientation in assemblies changed
    [ElectromagnetAssembly.SLDASM, Electromagnetic Actuator.SLDASM, KLink2.SLDPRT, SmallPipeExtension.SLDPRT]
2022-08-26 redesigned for fab and added a presentation file
    [50kg Load cell.stp, BallValveAssembly.SLDASM, BallValveAssembly.step, Coil.SLDPRT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]
2022-08-30 major design change support the servo
    [BallValve.SLDASM, BallValveAssembly.SLDASM, Coil.SLDPRT, CollectionTank.SLDASM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]
2022-08-30 changed the servo motor mount
    [BallValve.SLDASM, CrankLink.SLDPRT, DischargeFlowControlAssembly.SLDASM, DiversionSupport.SLDPRT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]
2022-08-31 update the designs to accomodate the big change
    [Assembly.SLDASM, BallValve.SLDASM, BallValveWithStrapsAssembly.SLDASM, BottomWasher.SLDPRT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]
2022-08-31 deleted FEA static analysis files
    [Assembly.SLDASM, BallValve.SLDASM, BallValveWithStrapsAssembly.SLDASM, BottomWasher.SLDPRT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]
2022-08-31 added the final presentation
    [DiversionSupport.SLDPRT, FlapAssembly.SLDASM, FlapHolder.SLDPRT, Interface.SLDPRT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]
2022-09-02 edited parts to support m16x2 nuts and bolts
    [DiversionSupport.SLDPRT, FlapHolder.SLDPRT, LA-T8.SLDASM, LA-T8Assembly.SLDASM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]
2022-10-30 refactored presentation file with composer
    [BallValve.SLDASM, CollectionTank.SLDASM, CollectionTankWithTheLoadCells.SLDASM, CompassSpike.SLDPRT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]
